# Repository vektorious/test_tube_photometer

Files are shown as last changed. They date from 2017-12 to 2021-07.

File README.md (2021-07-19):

<p align="center">
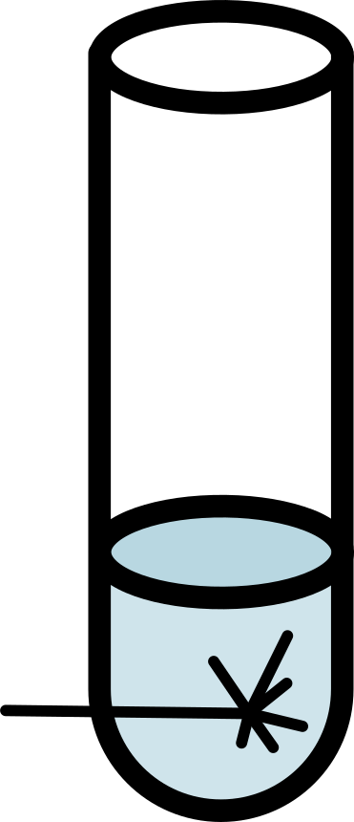
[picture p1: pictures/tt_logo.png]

<h1 align="center">Test Tube Photometer <br>
Flow-through Photometer
</h1>
<h3 align="center">Low-cost hardware setup for measuring light extinction and optical densities</h3>
</p>
<br>

## Welcome!

You can find a description on how to build the OLD VERSION of the photometer [here](https://alexanderkutschera.com/2017/12/09/photometer-shopping-list.html).

- [What's this all about?](#background)
- [How can I build my own photometer?](#building-instructions)
- [How can I contribute?](#contributing)
- [Wait, why should I contribute?](#report-issues)
- [Who is behind all this?](#who-is-behind-all-this)

### Background

This photometer can be used for science. We published a paper about it in [Current Microbiology](https://link.springer.com/article/10.1007/s00284-017-1370-3). (Yes, the journal has a paywall. It maybe was not the right decision to publish it there but I'm trying to make up for it by providing all info here in the repository. If you want the paper I can send it to you. Just drop me an [email](mailto:alexander.kutschera@gmail.com).)

#### What's a photometer?
Photometers are used to measure light extinction in liquids to analyse their content. They basically shine light through a certain amount of the liquid from one side and measure the light that's left on the other side. Among other things, photometers are used to measure the densities of bacterial cultures on a regular basis. You can determine them by comparing photometer measurements of culture media with (sample value) and without bacteria (blank value). Using physical laws you can then calculate the optical density of your sample.

#### Why a test tube photometer?
Well, I'm a lazy person. In order to measure the optical density of my bacterial cultures I always had to take a sample from them. This usually meant I had to work sterile to avoid contamination of my cultures which is a bit time consuming. That's why I asked myself if there is a way to measure the density directly in the test tube without having to open it. There are already some test tube photometer out there but they are expensive and often require the use of specific test tubes. That's why I started to develop a photometer which I could use with the standard test tubes.

<p align="center">
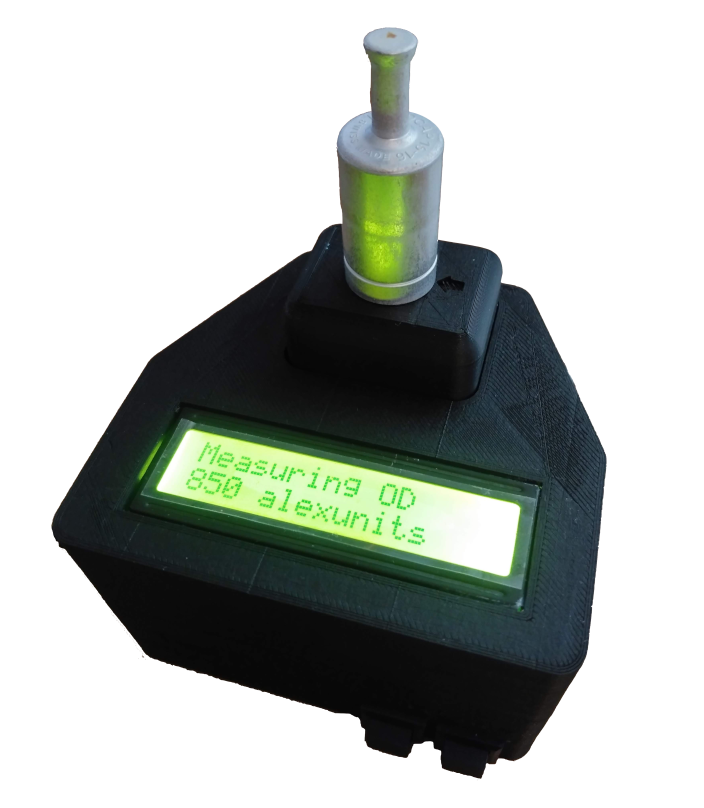
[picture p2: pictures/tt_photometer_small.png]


#### And why a flow-through photometer?
With a flow-through photometer can be used to monitor light extinction in any liquid independent of the container. The sample is constantly pumped through the photometer and OD is measured over time. I started to work on a flow-through version of the test tube photometer as part of a [Biomaker](https://www.biomaker.org/) project. We were developing an [low-cost microbial bioreactor](https://www.hackster.io/open-bioeconomy-lab/microbial-bioreactor-d7f61b) and I was looking into ways to measure the culture density in the device over time. But you can also use it for example to measure culture densities in a beaker or monitor the turbidity of river water.

<p align="center">
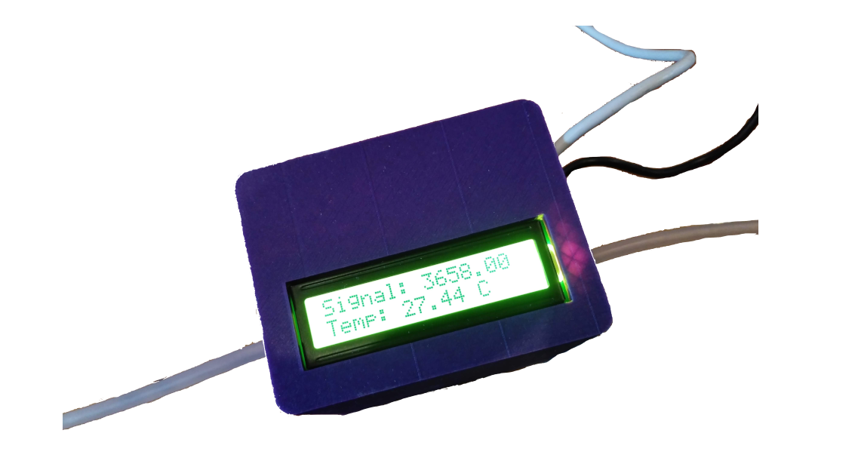
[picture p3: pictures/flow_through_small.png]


### Assembly instructions

The photometer is designed to be modular. You can add as many measurement cells as you like (well ok. you are limited by the amounts of analog inputs your microcontroller has).

There are two was of building the photometer:

#### 1. Using a breadboard and cables

**Advantage:**
You don't need many special parts apart from the sensor (opt101). Some cables, resistors and a breadboard are required as well.

**Disadvantage:**
The connections are not very stable which could produce reading errors. Wiring the opt101 just with cable is a bit confusing (at least it was for me). Apart from that, the legs of the sensor break easily if you bend them to often and too much.

#### 2. Using PCBs (Arduino Nano HAT and the sensor PCB)

**Advantage:**
All the electronics are easy to put together. The connections are stable and secure. You can quickly add connect more measurement cells.

**Disadvantage:**
Well.. you need the PCBs. But you can easily order them from a PCB manufacturer with the gerber files in this repository. You'll find more info about this in [/hardware/pcb/README.md](https://github.com/vektorious/test_tube_photometer/tree/master/hardware/pcb).

Both ways of building the photometer are described [in the instructions folder](https://github.com/vektorious/test_tube_photometer/tree/master/instructions).

### Contributing

This is a side project of mine and it is not actively developed. I work on it sometimes and try to improve the design and fix errors. I try to do my best to document it as good as possible so anybody can copy this and build their own photometer. You are welcome to contribute to the project by adding more designs for the housing and improving the building instructions.

### Report issues

Notice a mistake or errors? Please file any bugs, requests, or questions in the [issue tracker](https://github.com/vektorious/test_tube_photometer/issues)!

If you are new to GitHub issue tracker take a look [here](https://guides.github.com/features/issues/).

### Who is behind all this?

Please contact me if you have any questions.

<p align="center">
 </br>This work is licensed under a <a rel="license" href="http://creativecommons.org/licenses/by-sa/4.0/">Creative Commons Attribution-ShareAlike 4.0 International License</a>.
</p>

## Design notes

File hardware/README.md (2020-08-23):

# Information about the hardware components

## PCBs

TODO

- redo Arduino nano HAT
- add assembly instructions
- add BOM

## Housing

TODO

- add all stl
- redo the designs in openSCAD

<p align="center">
 </br>This work is licensed under a <a rel="license" href="http://creativecommons.org/licenses/by-sa/4.0/">Creative Commons Attribution-ShareAlike 4.0 International License</a>.
</p>

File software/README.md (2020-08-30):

# Scripts

## Arduino
Microcontroller scripts.

**Folder structure**
```
arduino
├── I2C_scanner
├── multiple
│   ├── calibrate_modules
│   ├── LCD_test_opt101
│   └── test_tube_ALK
└── single
    ├── set_sensitivity
    ├── test_everything
    ├── test_opt101_LED
    └── tt_photometer_single

```

## Python
Scripts for computer <--> microcontroller communication.
**Folder structure**
```
python_scripts
├── dataStream.py
├── dataStream_wo.py
├── serialMeasure.py
└── serialTest.py
```

<p align="center">
 </br>This work is licensed under a <a rel="license" href="http://creativecommons.org/licenses/by-sa/4.0/">Creative Commons Attribution-ShareAlike 4.0 International License</a>.
</p>

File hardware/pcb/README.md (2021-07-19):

# Test Tube Photometer PCBs

For full project details see [the main README](https://github.com/vektorious/test_tube_photometer#readme).

## tt_nano_HAT_b1

[Kitspace page](https://kitspace.org/boards/github.com/vektorious/test_tube_photometer/tt_nano_HAT_b1)

First version of a Arduino Nano HAT to connect multiple photometer cells.
It works BUT.

Problems:
- jst connectors too close together

## tt_nano_HAT_b2

[Kitspace page](https://kitspace.org/boards/github.com/vektorious/test_tube_photometer/tt_nano_HAT_b2)

Second version of the Arduino Nano HAT.
It looks better and works BUT.

Problems:
- connections/annotation screwed up.

(I'll never learn)

## opt101_module

[Kitspace page](https://kitspace.org/boards/github.com/vektorious/test_tube_photometer/tt_opt101_module)

PCB that fits the opt101 and a potentiometer to set the sensitivity of the sensor. Works great and fits perfectly into the housing of the measurement cells.

<p align="center">
 </br>This work is licensed under a <a rel="license" href="http://creativecommons.org/licenses/by-sa/4.0/">Creative Commons Attribution-ShareAlike 4.0 International License</a>.
</p>

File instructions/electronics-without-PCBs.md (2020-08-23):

# Setting up the electronics using wires and a breadboard.

TODO

- [Old instructions of the flow-through photometer](https://github.com/Biomaker/2018-opensourcebioreactor/tree/master/photometer)

- [Old instructions for the test tube photometer](https://alexanderkutschera.com/2017/12/09/photometer-shopping-list.html)

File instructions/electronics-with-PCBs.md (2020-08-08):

# Setting up the electronics using the PCBs

TODO

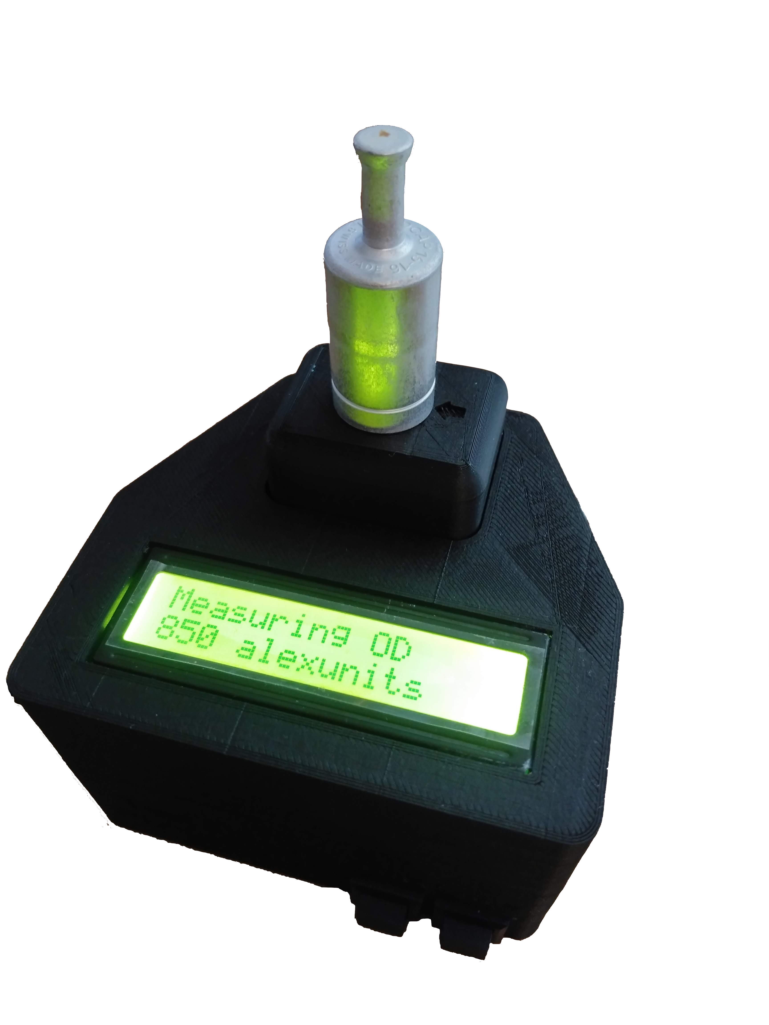
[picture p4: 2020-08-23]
pictures/tt_photometer.png

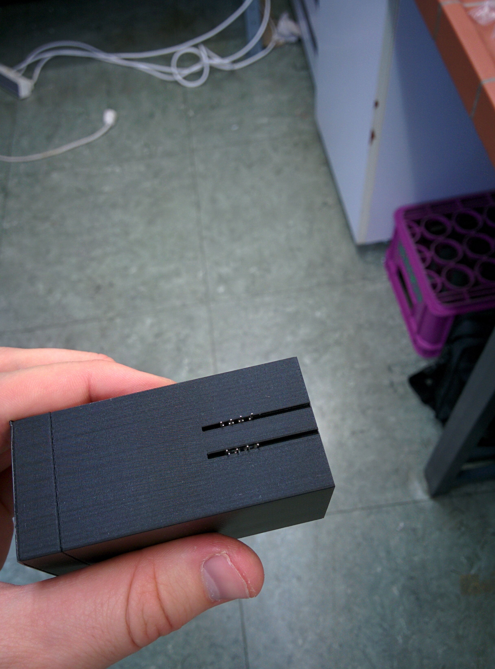
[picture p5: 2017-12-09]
pictures/cell_cover_3.jpg

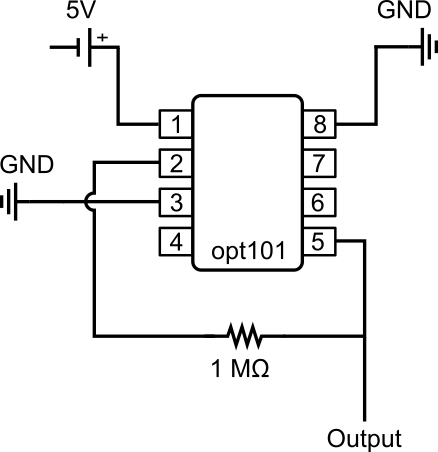
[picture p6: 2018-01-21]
pictures/sketch3.png

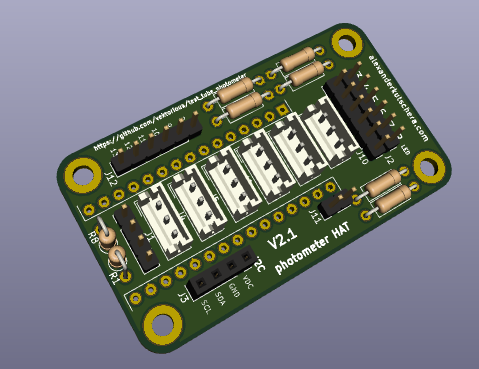
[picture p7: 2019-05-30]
pictures/3Drendered_pHAT.png

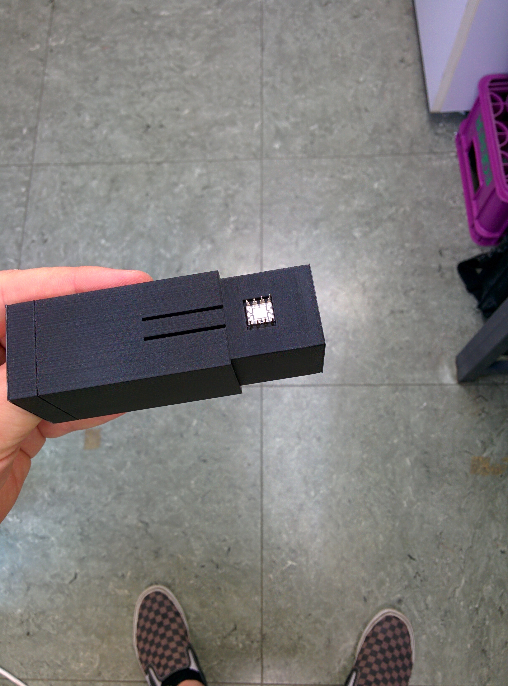
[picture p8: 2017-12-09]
pictures/cell_cover_1.jpg

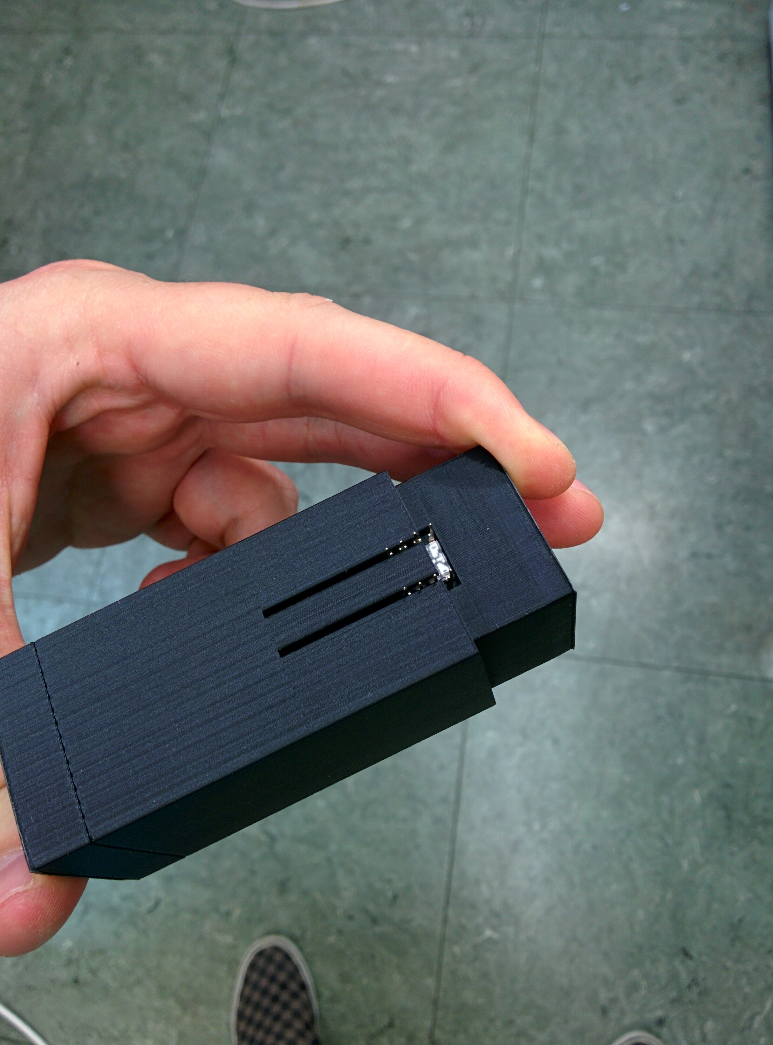
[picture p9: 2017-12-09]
pictures/cell_cover_2.jpg

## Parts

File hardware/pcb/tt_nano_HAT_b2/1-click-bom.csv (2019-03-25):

References | Qty | Description | Manufacturer | MPN | Digikey | Mouser | RS | Newark | Farnell
A1 | 1 | Arduino Nano v3.x
J1 | 1 | Pin Header 04 2.54mm | Molex | 22-03-2041 | WM4002-ND | 53822032041 | 467560P | 26M6328 | 9731091
J2, J10 | 2 | Pin Header 6 2.54 mm | Molex | 22-03-2061 | WM4004-ND | 53822032061 | 479181 | 26M6330 | 9731113
J3 | 1 | Female Header 1x4 2.54 mm | Harwin | M20-7820446 | 952-1792-ND | 855M207820446 | 6816814 | 38K5904 | 7991932
J9, J8, J7, J6, J5, J4 | 6 | JST EH B3B-EH-A 1x03 P2.50mm Vertical | JST | B3B-EH-A(LF)(SN) | 455-1612-ND |  | 5151399 | 53X3091 | 2399161
R1, R8 | 2 | 10k Axial | TE Connectivity | ROX3SJ10K | A106020CT-ND | 279ROX3SJ10K | 2142897 | 34R4864 | 1738702
R2, R3, R4, R5, R6, R7 | 6 | 220 Axial Resistor | TE Connectivity | C14220RJL | A141517CT-ND | 279CFR25J220R | 6661623 | 43AC3068 | 2805141
S1, S2 | 2 | Pushbutton Switch (optional) | Eledis | SED1GI-2H
S3 | 1 | Rocker Switch (optional) | Arcolectric | H8600VBABP

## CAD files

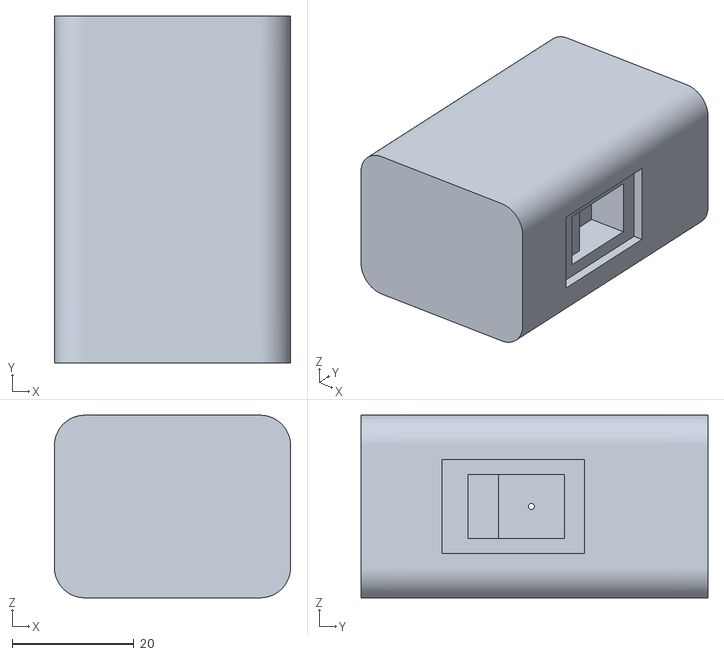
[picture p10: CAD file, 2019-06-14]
hardware/3Dfiles/cell/c_cell_main.stl
38.8 x 57.0 x 30.0

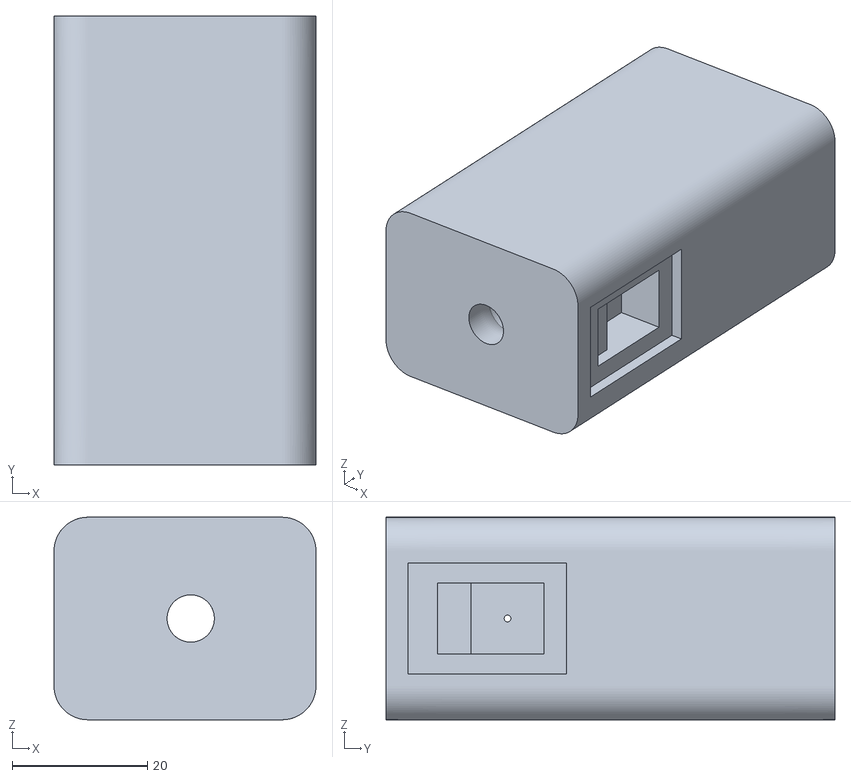
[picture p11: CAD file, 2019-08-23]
hardware/3Dfiles/kit_flow-through_photometer/ft_cell_main.stl
38.8 x 66.5 x 30.0

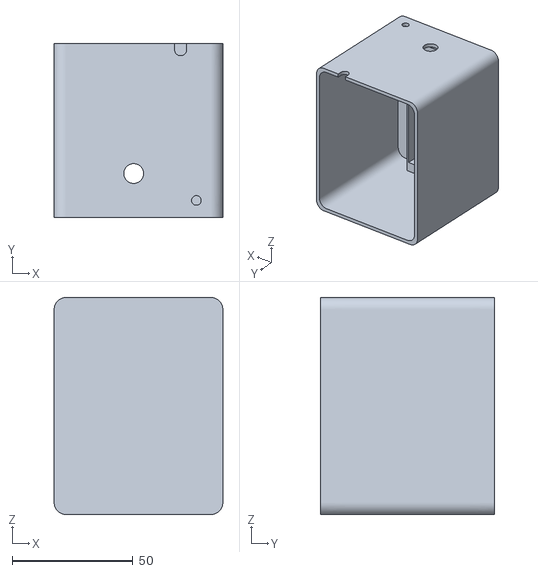
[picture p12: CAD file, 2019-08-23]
hardware/3Dfiles/kit_flow-through_photometer/housing_main.stl
70.0 x 72.0 x 90.0

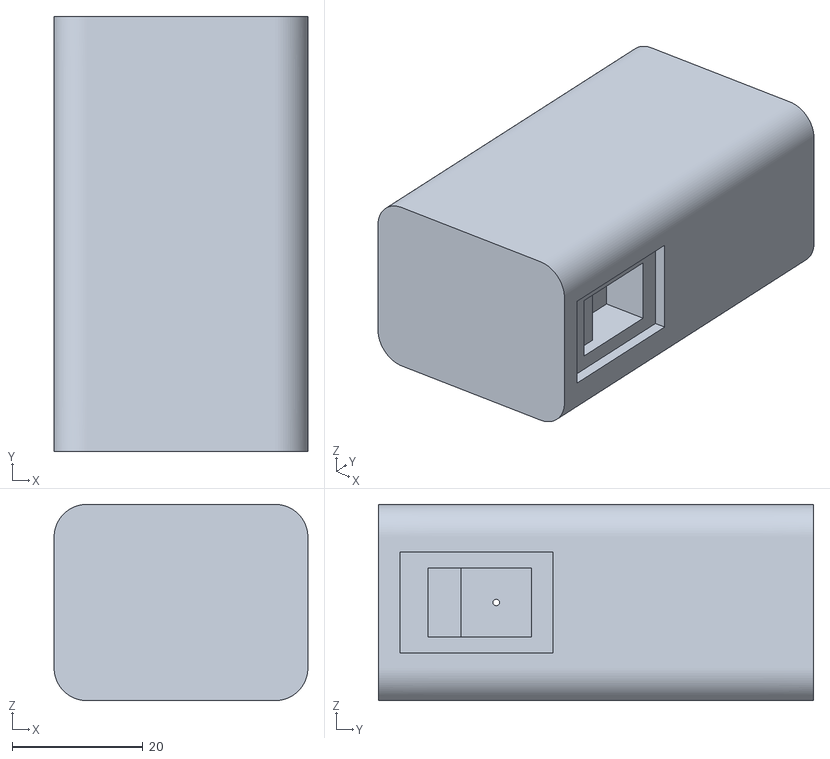
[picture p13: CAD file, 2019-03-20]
hardware/3Dfiles/cell/tt_cell_main.stl
38.8 x 66.5 x 30.0

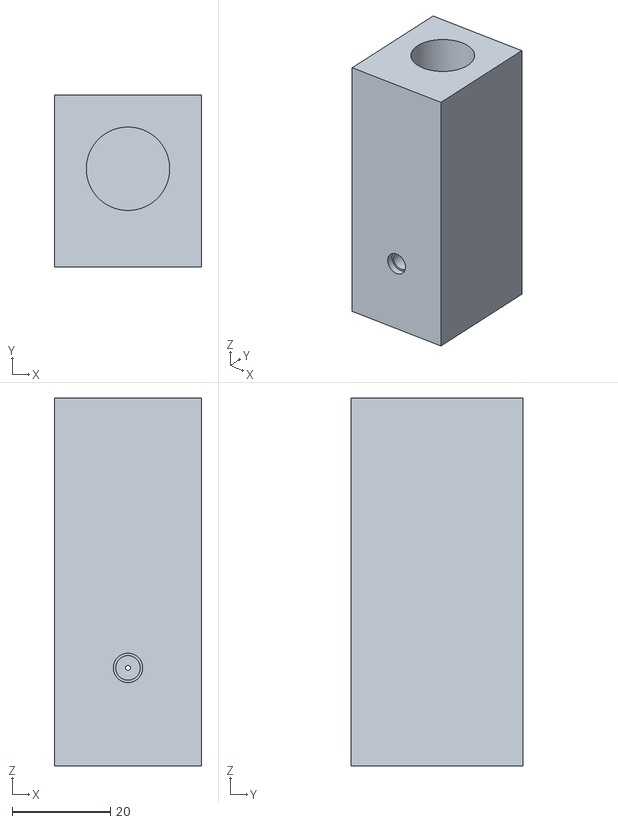
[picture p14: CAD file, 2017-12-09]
3Dfiles/housing.stl
30.0 x 35.0 x 75.0

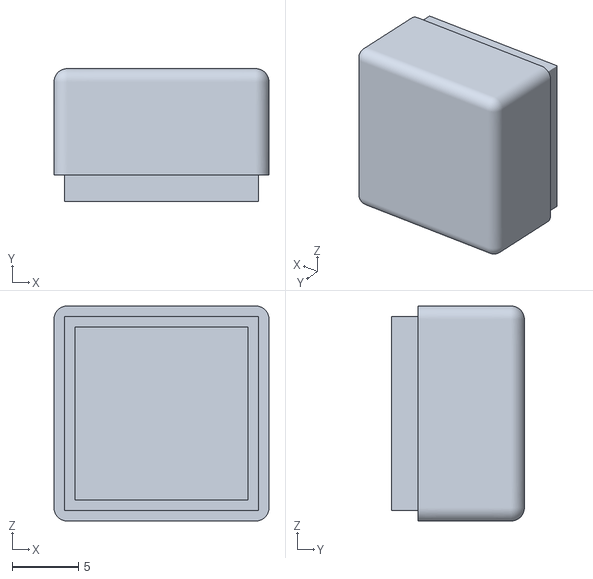
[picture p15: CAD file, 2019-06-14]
hardware/3Dfiles/cell/c_cell_cuvette_lid.stl
16.2 x 10.0 x 16.2

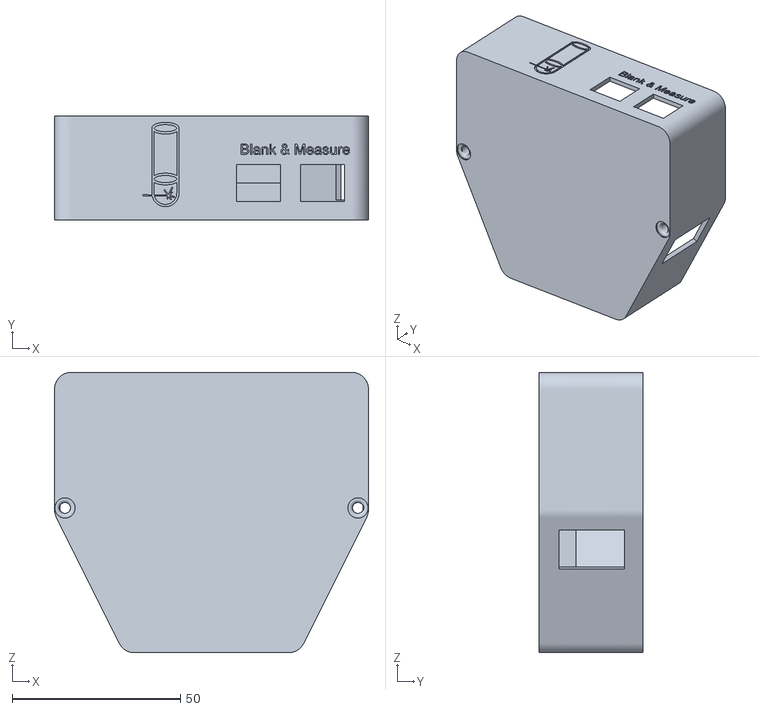
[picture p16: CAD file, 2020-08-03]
hardware/3Dfiles/housing/single_tt_b1/housing_bottom.stl
93.2 x 31.0 x 83.2

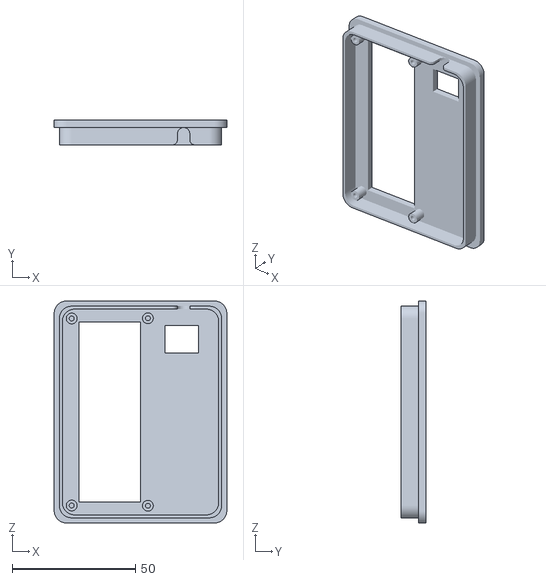
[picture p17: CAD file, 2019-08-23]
hardware/3Dfiles/kit_flow-through_photometer/housing_lid.stl
70.0 x 10.0 x 90.0

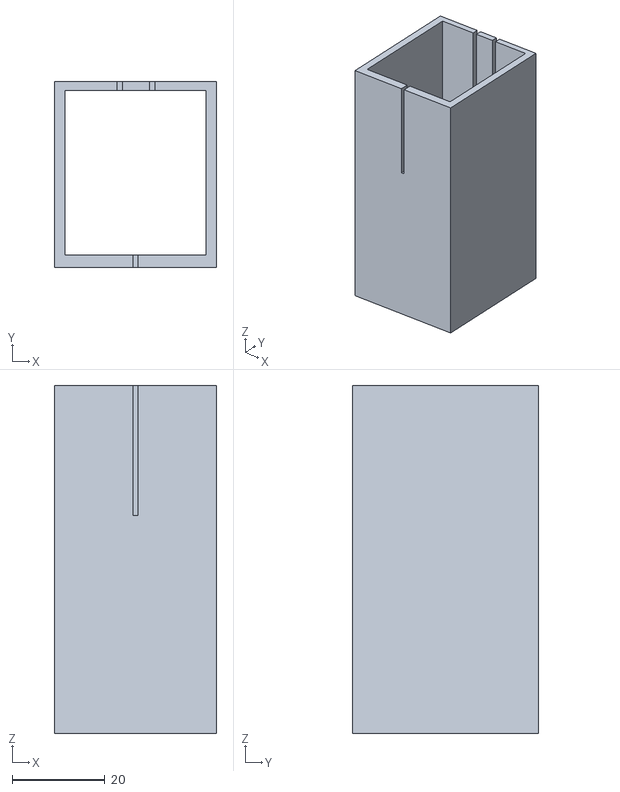
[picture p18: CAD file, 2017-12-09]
3Dfiles/housing_cover.stl
35.0 x 40.0 x 75.0

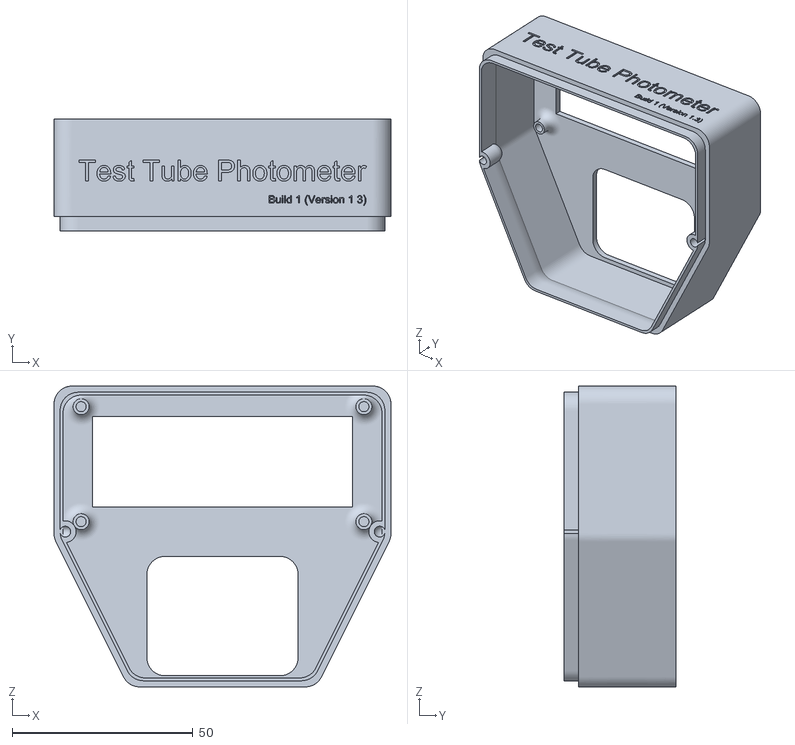
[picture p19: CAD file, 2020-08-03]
hardware/3Dfiles/housing/single_tt_b1/housing_top.stl
93.2 x 31.0 x 83.2

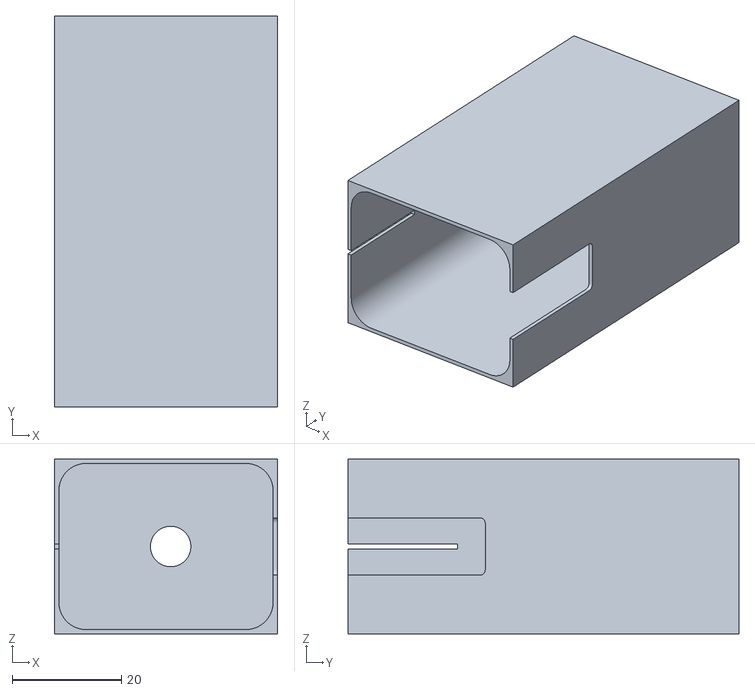
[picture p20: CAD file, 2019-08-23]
hardware/3Dfiles/kit_flow-through_photometer/ft_cell_cover.stl
40.8 x 71.5 x 32.0

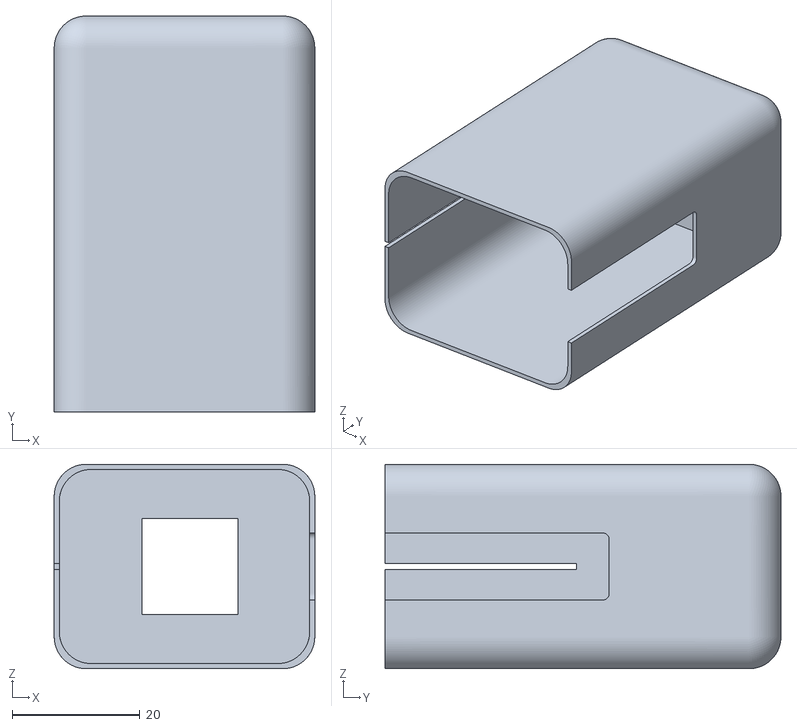
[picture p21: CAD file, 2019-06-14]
hardware/3Dfiles/cell/c_cell_cover.stl
40.8 x 62.0 x 32.0

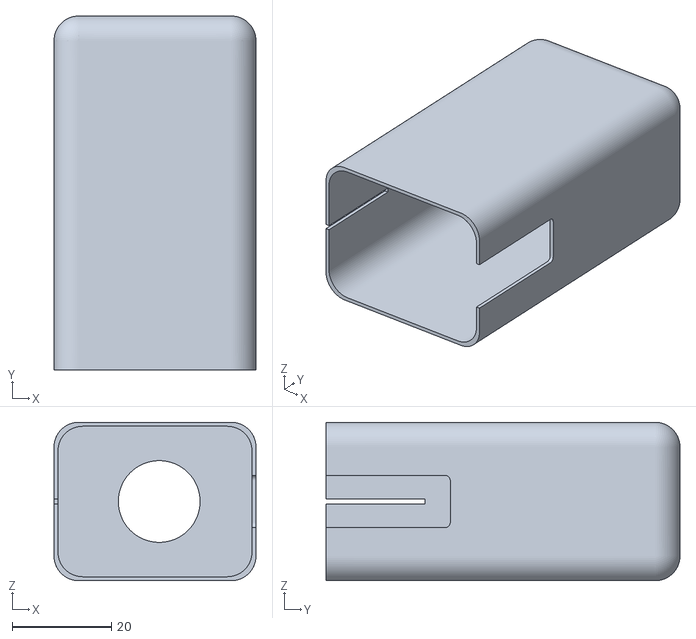
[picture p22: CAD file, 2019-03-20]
hardware/3Dfiles/cell/tt_cell_cover.stl
40.8 x 71.5 x 32.0

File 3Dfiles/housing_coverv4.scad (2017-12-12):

module example003()
{
	difference() {
		union() {
			translate([-1.5, -5, 0])
				cube([35, 40,  75], center = false);	

			
		}
		union() {
            translate([0.8, -2.3, 0])
				cube([30.4, 35.4,  75], center = false);
            translate([30.1-11-0.1 , 31, 47])
				cube([1.2, 5, 28], center = false);
            translate([0.9+11+0.1, 31, 47])
				cube([1.2, 5, 28], center = false);
            translate([16, -3, 33+28])
                cube([1, 5, 28], center = true);
}
	}
}

example003();

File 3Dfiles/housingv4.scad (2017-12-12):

module example003()
{
	difference() {
		union() {
			translate([-1.5, -5, 0])
				cube([30, 35,  75], center = false);	
			//translate([25, -5, 0])
				//cube([3.5, 10, 65], center = false);	
			//translate([-1.5, 5, 0])
				//cube([3.5, 3.5, 65], center = false);
			//translate([28, 13, 0])
				//cube([2.5, 3.5, 75], center = false);
			
		}
		union() {
			translate([13.5, 15, 5])
				cylinder(h = 100, r = 8.5, center = false, $fn = 100); //tube 
			translate([13.5, 6, 20])
				rotate(90, [1, 0, 0]) cylinder(h = 20, r = 2.5, center = false, $fn = 100); //led
            translate([13.5, -3.1, 20])
				rotate(90, [1, 0, 0]) cylinder(h = 2, r = 3, center = false, $fn = 100); //led
			translate([13.5, 50, 20])
				rotate(90, [1, 0, 0]) cylinder(h = 50, r = 0.5, center = false, $fn = 100); //apature
			translate([13.5, 30, 20])
				cube([6.2, 10, 10], center = true); //sensor
			translate([13.5, 30, 20])
				cube([11, 3.5, 10], center = true); //sensor wires
			//translate([13.5, 30, 96])
				//cube([32, 8, 10], center = true);	 //multiple sensor wire channel
			//translate([13.5, 0, 70])
				//cube([4, 10, 100], center = true);	 //led wires
			//translate([13.5, 0, 96])
				//cube([32, 1, 10], center = true);	 //multiple led wire channel
			//translate([24, 28, -0.5])
				//cube([6, 5, 92], center = false);	
			//translate([-2, -2, -0.5])
				//cube([5, 4, 92], center = false);	
			//translate([-2, 13, -0.5])
				//cube([2.5, 4.5, 110], center = false);	
}
	}
}

example003();

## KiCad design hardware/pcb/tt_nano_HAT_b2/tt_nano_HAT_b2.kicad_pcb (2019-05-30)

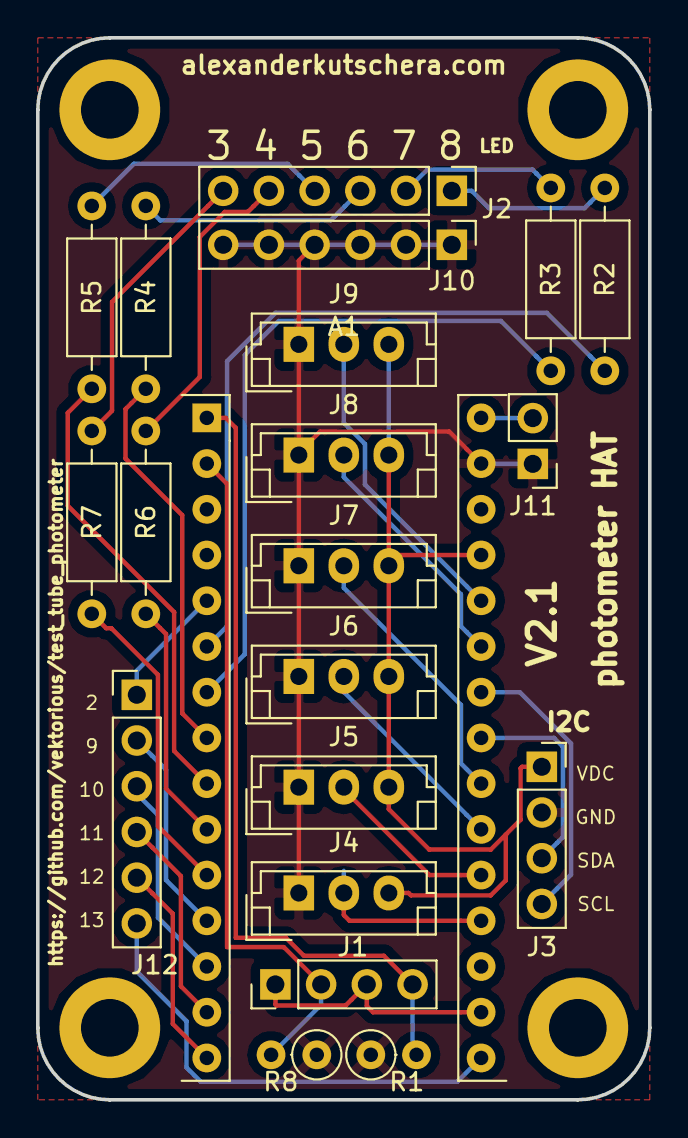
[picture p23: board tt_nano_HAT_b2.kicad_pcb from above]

Board: 2 copper layers, 34.0 x 59.0 mm, 21 parts (0 on the bottom side), 32 nets.

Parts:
A1: Arduino_Nano_v3.x; Arduino_Nano2
J1: Conn_01x04_Male; PinHeader_1x04_P2.54mm_Vertical
J2, J10, J12: Conn_01x06_Male; PinHeader_1x06_P2.54mm_Vertical
J3: Conn_01x04_Female; PinSocket_1x04_P2.54mm_Vertical
J4, J5, J6, J7, J8, J9: Conn_01x03_Male; JST_EH_B03B-EH-A_1x03_P2.50mm_Vertical
J11: Conn_01x02_Male; PinHeader_1x02_P2.54mm_Vertical
R1, R8: R; R_Axial_DIN0207_L6.3mm_D2.5mm_P2.54mm_Vertical
R2, R3, R4, R5, R6, R7: R; R_Axial_DIN0207_L6.3mm_D2.5mm_P10.16mm_Horizontal

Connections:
GND: A1.29, J3.2, J4.1, J5.1, J6.1, J7.1, J8.1, J9.1, J10.1, J10.2, J10.3, J10.4, J10.5, J10.6, J11.1, R1.1, R8.1
unnamed: A1.1, J1.4, R1.2
unnamed: A1.2, J1.2, R8.2
unnamed: A1.5, J12.1
unnamed: A1.6, R2.1
unnamed: A1.7, R3.1
unnamed: A1.8, R4.1
unnamed: A1.9, R5.1
unnamed: A1.10, R6.1
unnamed: A1.11, R7.1
unnamed: A1.12, J12.2
unnamed: A1.13, J12.3
unnamed: A1.14, J12.4
unnamed: A1.15, J12.5
unnamed: A1.16, J12.6
unnamed: A1.17, J1.1, J1.3
unnamed: A1.19, J4.2
unnamed: A1.20, J5.2
unnamed: A1.21, J6.2
unnamed: A1.22, J7.2
unnamed: A1.23, J3.3
unnamed: A1.24, J3.4
unnamed: A1.25, J8.2
unnamed: A1.26, J9.2
unnamed: A1.27, J3.1, J4.3, J5.3, J6.3, J7.3, J8.3, J9.3
unnamed: A1.30, J11.2
unnamed: J2.1, R2.2
unnamed: J2.2, R3.2
unnamed: J2.3, R4.2
unnamed: J2.4, R5.2
unnamed: J2.5, R6.2
unnamed: J2.6, R7.2

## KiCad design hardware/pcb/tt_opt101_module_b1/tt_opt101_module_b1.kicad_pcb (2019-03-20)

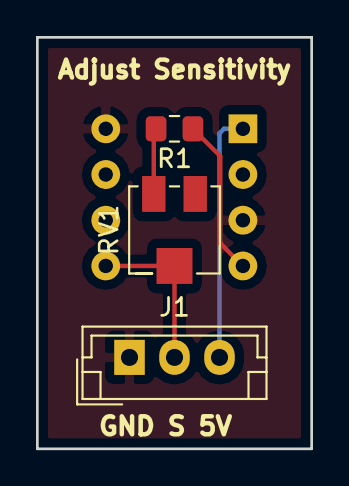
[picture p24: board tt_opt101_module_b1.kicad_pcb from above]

Board: 2 copper layers, 15.2 x 22.9 mm, 4 parts (1 on the bottom side), 5 nets.

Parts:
J1: Conn_01x03_Male; JST_EH_B03B-EH-A_1x03_P2.50mm_Vertical
O1: opt101; DIP-8_W7.62mm
R1: R; R_0805_2012Metric_Pad1.15x1.40mm_HandSolder
RV1: R_POT; Potentiometer_Bourns_3214J_Horizontal

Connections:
+5V: J1.3, O1.1
GND: J1.1, O1.3, O1.8
unnamed: J1.2, O1.5, RV1.2
unnamed: O1.4, R1.1
unnamed: R1.2, RV1.1

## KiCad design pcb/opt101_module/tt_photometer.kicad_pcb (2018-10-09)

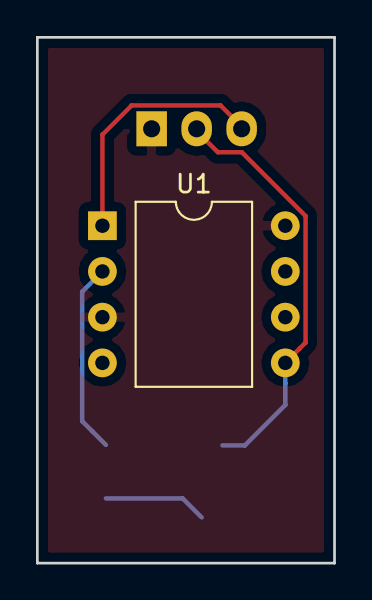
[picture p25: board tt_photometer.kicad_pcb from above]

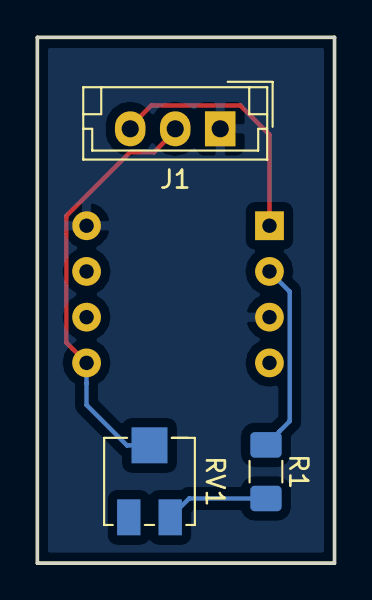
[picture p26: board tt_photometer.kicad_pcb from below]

Board: 2 copper layers, 16.5 x 29.2 mm, 4 parts (3 on the bottom side), 5 nets.

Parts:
J1: Conn_01x03_Male; JST_EH_B03B-EH-A_1x03_P2.50mm_Vertical
R1: R; R_1206_3216Metric_Pad1.42x1.75mm_HandSolder
RV1: R_POT; Potentiometer_Bourns_3214J_Horizontal
U1: opt101; DIP-8_W10.16mm

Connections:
+5V: J1.3, U1.1
GND: J1.1, U1.3, U1.8
unnamed: J1.2, RV1.2, U1.5
unnamed: R1.1, U1.2
unnamed: R1.2, RV1.1

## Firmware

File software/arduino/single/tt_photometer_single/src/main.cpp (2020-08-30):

// Version 1.3 of the test tube photometer software
// It ignores possible disturbing light by neglecting the "dark values"
#include <Arduino.h>
#include <LiquidCrystal_I2C.h>

// Set the LCD address to 0x3F for a 16 chars and 2 line display
// adjust first parameter to the I2C address of your LCD. Check it via the I2C scanner
LiquidCrystal_I2C lcd(0x3F, 16, 2);

// Input/Output
int sensor = A1;  // input pin of OPT101 attached to Analog 1
int buttonBlank = 9; // input pin for blank button
int buttonMeasure = 10; // input pin for measure button
int LED = 8; // output pin for blank button

// Variables
float opt_signal;
float OD = 0;
int blank = 0;
float blankValue = 0;
int measure = 0;

// Add factor from calibration curve to calculate concentration
int factor = 0;

bool trouble = false;
bool blanked = false;

// Function for "Blank" measurements
void measureBlank(int multiplier) { // multiplier determines how many measurements are pooled
  blankValue = 0;
  
  for (int dummy = 0; dummy < multiplier; dummy++){
    delay(100);
    blankValue = (blankValue + analogRead(sensor));
    delay(100);
  }
  
  blankValue = blankValue/multiplier;
  blanked = true;
}

// Function for OD measurements
void measureOD(int multiplier) { // multiplier determines how many measurements are pooled
  opt_signal = 0;

  for (int dummy = 0; dummy < multiplier; dummy++){
    delay(100);
    opt_signal = (opt_signal + analogRead(sensor));
    delay(100);
  }

  if (blanked == true){ // output of OD if blanked
    opt_signal = opt_signal/multiplier;
    OD = -log10(opt_signal/blankValue);
    if(factor =! 0){
      OD = OD*factor;
    }
  }

  else{ // output of the raw value if not blanked
    OD = opt_signal/multiplier;
  }
}

// Start loop
void setup() {

  delay(100);

  // Turn on the blacklight and print a message.
  lcd.begin();
  lcd.backlight();
  lcd.print("   Test  Tube    ");
  lcd.setCursor(0, 1);
  lcd.print("Photometer  v1.3");

  pinMode (LED, OUTPUT); //for LED
  pinMode(buttonBlank, INPUT_PULLUP);
  pinMode(buttonMeasure, INPUT_PULLUP);
  delay(1000);
  lcd.clear();

  // If any button is pressed during the startup, troubleshooting mode is activated.
  // (LED is always on & raw value output) 
  for (int i = 0; i < 10; i++){
    lcd.setCursor(0, 0);
    lcd.print("Starting ... ");
    lcd.print(i);
    measure = digitalRead(buttonMeasure);
    blank = digitalRead(buttonBlank);
    delay(500);
    if (measure == LOW || blank == LOW){
      trouble = true;
      lcd.clear();
      lcd.print("Troubleshooting");
      lcd.setCursor(0, 1);
      lcd.print("Mode");
      delay(1000);
      break;
    }
  }
  
  lcd.clear();
  lcd.print("Press Button");
  lcd.setCursor(0, 1);
  lcd.print("to start :)");
}

// Main loop
void loop() {
  measure = digitalRead(buttonMeasure);
  blank = digitalRead(buttonBlank);

  // troubleshooting mode
  if (trouble == true){
    lcd.clear();
    lcd.print("Showing raw signal ...");
    lcd.setCursor(0, 1);
    digitalWrite(LED, HIGH);
    delay(100);
    lcd.print(analogRead(sensor));
    delay(500);
  }

  // measuring blank
  else if(blank == LOW){
    lcd.clear();
    lcd.print("Measuring Blank ...");
    lcd.setCursor(0, 1);
    lcd.print("Please wait");
    digitalWrite(LED, HIGH);
    delay(500);
    measureBlank(10);
    digitalWrite(LED, LOW);
    lcd.setCursor(0, 1);
    lcd.print("                ");
    lcd.setCursor(0, 1);
    lcd.print("Blanked");
  }
  
  // measuring sample
  else if(measure == LOW){
    lcd.clear();
    lcd.print("Measuring OD ...");
    lcd.setCursor(0, 1);
    lcd.print("Please wait");
    digitalWrite(LED, HIGH);
    delay(500);
    measureOD(10);
    digitalWrite(LED, LOW);

    

    lcd.setCursor(0, 1);
    lcd.print("                ");
    lcd.setCursor(0, 1);
    lcd.print(OD);

    if (factor =! 0){
      lcd.print(" g/L");
    }

    else if(blanked == false){
      lcd.print(" raw value");
    }
  }
}

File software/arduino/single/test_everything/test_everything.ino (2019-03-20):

#include <LiquidCrystal_I2C.h>

// Set the LCD address to 0x27 for a 16 chars and 2 line display
LiquidCrystal_I2C lcd(0x27, 16, 2); // adjust first parameter to the I2C address of your LCD. Check it via the I2C scanner


int sensor = A1;  // output pin of OPT101 attached to Analog 5
int opt_signal;
int LED = 5;
int buttonBlank = 12;
int buttonMeasure = 13;

int blank = 0;
int blanked = 0;
int measure = 0;

void setup() {
  Serial.begin(9600);
  delay(100);
  lcd.begin();

  // Turn on the blacklight and print a message.
  lcd.backlight();
  lcd.print("Measuring OD");
  
  pinMode (LED, OUTPUT); //for LED
  pinMode(buttonBlank, INPUT);
  pinMode(buttonMeasure, INPUT);
}

void loop() {
  opt_signal = analogRead(sensor);
  measure = digitalRead(buttonMeasure);
  blank = digitalRead(buttonBlank);
  delay(1000);

  if (measure == HIGH){
    Serial.print("Measure was pressed");
    Serial.print("\n");
  }

    if (blank == HIGH){
    Serial.print("Blank was pressed");
    Serial.print("\n");
  }
  
  Serial.print(opt_signal);
  Serial.print("\n");
  digitalWrite(LED, !digitalRead(LED)); // alternating LED on and off

  lcd.setCursor(0, 1);
  lcd.print(opt_signal);
  lcd.print(" alexunits");

}

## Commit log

2018-10-06 added kitcad
    [tt_photometer.kicad_pcb, tt_photometer.sch]
2018-12-04 Created PCBs
    [tt_nano_HAT-B.Adhes.gbr, tt_nano_HAT-B.Cu.gbr, tt_nano_HAT-B.Mask.gbr, tt_nano_HAT-B.Paste.gbr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]
2019-03-20 Updated PCB and 3D files
2019-03-20 reorganized repo
    [cell_cover.stl, cell_main.stl, housing.scad, housing.stl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]
2019-03-21 Included BOM
    [1-click-bom.tsv, tt_nano_HAT_b1.sch]
2019-03-25 uploaded new .stl and BOM
    [1-click-bom.csv, 1-click-bom.tsv, housing_bottom.stl, tt_nano_HAT_b1.sch]
2019-05-30 update pcb
    [1-click-bom.csv, tt_nano_HAT_b2-B.Adhes.gbr, tt_nano_HAT_b2-B.Cu.gbr, tt_nano_HAT_b2-B.Mask.gbr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]
2019-06-10 uploaded cuvette cell stls
    [c_cell_cover.stl, c_cell_main.stl, tt_cell_cover.stl, tt_cell_main.stl]
2019-06-14 updated stls
    [c_cell_cover.stl, c_cell_cuvette_lid.stl, c_cell_main.stl]
2019-06-23 uploaded flow_through files
    [ft_cell_cover.stl, ft_cell_main.stl, housing_lid.stl, housing_main.stl]
2019-08-23 Updated flow-through housing
    [ft_cell_cover.stl, ft_cell_main.stl, housing_lid.stl, housing_main.stl]
2019-11-16 create OKH manifest to test tube photometer
2020-08-03 rework of repo
    [tt_nano_HAT_b2-B.Adhes.gbr, tt_nano_HAT_b2-B.Cu.gbr, tt_nano_HAT_b2-B.Mask.gbr, tt_nano_HAT_b2-B.Paste.gbr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]
2021-07-16 Add links to pcb readme
2021-07-16 Fix link to hardware/pcb readme
